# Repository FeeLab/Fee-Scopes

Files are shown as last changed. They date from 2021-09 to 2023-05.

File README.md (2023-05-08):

# Getting Started

animation of neural activity recorded in a mouse using the Kiloscope

Welcome to the repository on all things related to the Featherscope and Kiloscope, two light-weight head-mounted microscopes developed in the Fee lab at MIT. Our intent with this repository is to give you all the information you need to build your own scopes to use in your lab. We are also excited about people developing their own upgrades or even using elements of this project for their own microscope designs. Please let us know if you have any feedback or suggestions for improving these resources--we are always looking for ways to make this project more useful to the community!

The microscopes described in this repository are featured in [this bioRxiv paper](https://www.biorxiv.org/content/10.1101/2021.09.03.458947v2). All the analysis code in the paper can be found at [this repository](https://github.com/FeeLab/Microscope-Paper-Code), and the raw data from the paper is posted [here](https://academictorrents.com/details/aa2a3d2f5ff0b3974871db47db57bc3dabf3c192).

A fully functional system is comprised of the microscope itself, a DAQ and acquisition computer, a laser and associated illumination optics, and (optionally) a commutator for long-term recording. The components necessary for each of these subsystems are listed in `main_bom.ods` along with a cost breakdown.



# Microscope

Each microscope is built from small optical components mounted inside 3D printed parts. The optics needed for each microscope can be found under the Kiloscope and Featherscope tabs of `main_bom.ods`. The STEP files for the printed parts are located in the `body_components` folder. Technical details about the construction process can be found in the Methods section of the paper.

## Aspheric Lenses

lens assembly

The aspheric lens assemblies used in the Kiloscope are taken from replacement rear camera modules for the Samsung Galaxy S9 phone. These modules can be purchased online from 3rd party vendors, however the lenses then need to be carefully removed from the assembled housing. Instructions for removing the lenses from the modules can be found in `assembly_instructions`. The process should take about 20 minutes for an experienced assembler. Note that the lens material is very easy to scratch and difficult to clean, so be careful not to touch the lens faces during this process! When you have extracted the lens, you can store it safely in a PDMS device carrier (we reuse the containers that Edmund Optics ships their prisms in).

## Ground GRIN Lenses

GRIN lens

The tube lens used in the Featherscope is a GRIN lens purchased from Edmund Optics that has been ground down to a total length of 1 mm. Ideally we would have GRINTech, the manufacturer of the original lenses, make us custom lenses with the correct length to begin with. However, GRINTech and Inscopix have signed an anticompetitive exclusive distribution agreement for one-photon calcium imaging, so we have to be a little more creative about how we get these components. We purchase lenses from Edmund Optics (part number in BOM) and have them ground down to 1.00 mm by Pioneer Precision Optics, a custom optics company based in Massachusetts.

## Fiber Bundles

The fiber bundle used in the Featherscope is made by [Acrolite](https://www.acrolite.net/products/micro-fiber-optics), a company based in New York that specializes in making impressively tiny and intricate optical fiber bundles with custom potted termination geometries. They have a great engineering department and will work with you on custom solutions if you want to design a different illumination path.



## 3D Prints

We have had success ordering prints from [Rosenberg Industries](https://www.rosenbergindustries.com), a company based in Minnesota that specializes in prints for neuroscience implant devices. Parts are printed in Formlabs Grey resin at 25 micron resolution.



## Printed Circuit Boards

We order our image sensor boards from [Speedy Circuits](http://www.speedy-circuits.com.tw/), a board house in Taiwan that specializes in small run fabrication and assembly. We highly recommend the additional cost of board assembly unless you really want to practice your BGA soldering skills! Boards can be ordered using the gerber files found in the `python_pcb` folder.

Here are the specifications for the boards if you want to order them from another board house.

| Parameter       | Value       |
| -----------     | ----------- |
| Layer Count     | 6           |
| Copper Weight   | 1.1 mil external, 0.7 mil internal |
| Board Thickness | 500 micron |
| Dimensions | 8.2 x 14.0 mm |
| Number of Holes | 146 |
| Min Hole Size | 3 mil |
| Blind Vias | L1-L4 |
| Min Trace/Space | 3 mil |
| Vias in Pad | Epoxy Filled and Plated |
| Surface Finish | Immersion gold, 2 micron |

The board design files are free to view with Altium but require an Altium license to edit. If you are a student, you can obtain an [educational license](https://www.altium.com/education/student-licenses) for free. Let us know if you would like to convert the design files to an open-source format like KiCad and we would be happy to assist.

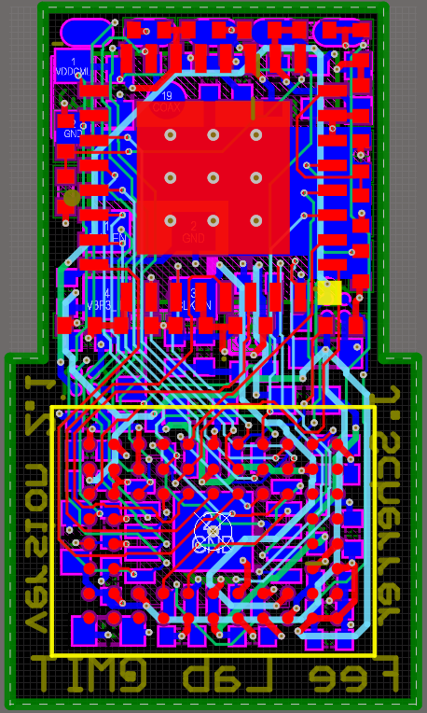
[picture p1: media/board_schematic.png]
Altium screenshot of schematic


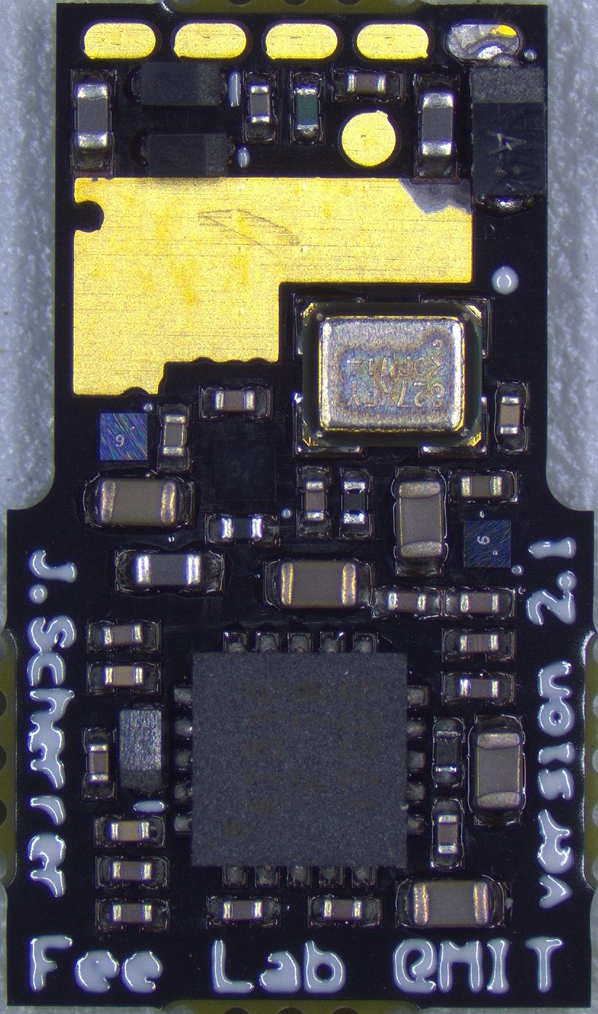
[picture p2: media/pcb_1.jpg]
top side of assembled pcb
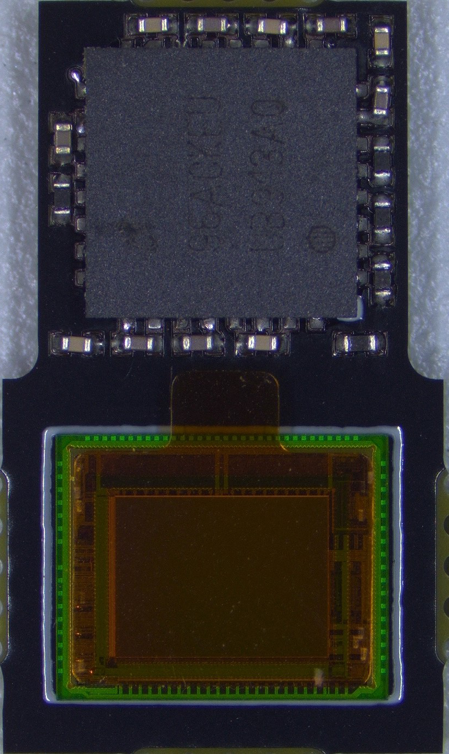
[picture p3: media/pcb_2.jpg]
bottom side of assembled pcb
 

## Assembly

Step-by-step instructions for assembling the microscopes are provided in `assembly_instructions`. Most components are secured using UV cure optical cement that can be purchased from [Edmund Optics](https://www.edmundoptics.com/f/norland-optical-adhesives/11818/) or a similar supplier. These instructions are a work in progress, so please don't hesistate to contact us if any of the steps are unclear!

## Programming

Firmware for the Attiny on the PCB can be found in `attiny_firmware`. Source code is included, with the exception of a section of `sensor_power_sequencing.c` that is restricted under NDA with Arrow, a distributor of ONSemi components. If you want access to the register settings contained in this section of the source code, contact an ONSemi distributor and request an NDA for the Python 480 programming notes.

The compiled code is contained in `Mscp_code/Release/Mscp_code.elf` and can be uploaded to the microcontroller using [Atmel Studio](https://microchipdeveloper.com/install:atstudio). We use [this programmer](https://www.microchip.com/en-us/development-tool/ATATMEL-ICE) but anything compatible with UPDI should work.

# DAQ System

## Hardware
The DAQ hardware is based on that of the [UCLA Miniscope](https://github.com/Aharoni-Lab/Miniscope-v4/wiki/DAQ-Hardware) and uses similar fabrication parameters. We had ours fabricated and assembled by [Seeed Studio](https://www.seeedstudio.com/) since these boards don't have as demanding specifications as the image sensor boards. Fabrication files can be found in the `DAQ` folder.

You will need to flash the firmware onto EEPROM before using the boards. Compile the DAQ firmware code in `cypress_firmware` using the [Cypress USB Suite](https://www.infineon.com/cms/en/design-support/tools/sdk/usb-controllers-sdk/ez-usb-fx3-software-development-kit/?utm_source=cypress&utm_medium=referral&utm_campaign=202110_globe_en_all_integration-software) and load it onto the board following the directions for the [UCLA Miniscope](https://github.com/Aharoni-Lab/Miniscope-DAQ-Cypress-firmware).

## Recording Software
The DAQ board presents itself to your computer as a webcam device, and for testing can be opened as a streaming device in [VLC](https://www.videolan.org/vlc/). For experiments, we acquire data from the microscope using [Bonsai](https://bonsai-rx.org/), a reactive programming languange designed for the multiple asynchronous data streams typical of behavioral neuroscience experiments. Bonsai has modules for recording from the UCLA Miniscope, Neuropixels, National Instruments devices, Arduinos, and various other data streams. We have written a module for our microscopes that can be downloaded from the Bonsai package manager. The module outputs video data in RGB565 format and allows for control of the image sensor gain. The source code can be found in `bonsai_module`.

An example Bonsai script for recording can also be found in `bonsai_module`. This script saves video from both the microscope and from an animal tracking camera simultaneously, while recording timestamps for each frame of both streams. Video is saved in the raw RGB565 format, but the script also performs realtime conversion to a human-interpretable grayscale image for online monitoring of the fluorescence signal.

Capture

# Illumination Optics

## Laser
Illumination light is provided by a multimode 473 nm laser similar to those used in optogenetics experiments. We use the MBL-473-50mW laser from [CNI Laser](http://www.cnilaser.com/), an optics company based in China with a wide range of turnkey optical systems for neuroscience applications. If you are planning on imaging at a different wavelength or have other specific requirements, they will probably be able to match your requirements.

## Coupling Optics
Light from the laser is coupled into the fiber using a system of optics detailed in the methods section of the paper and in `main_bom.ods`. Optics are assembled in a Thorlabs cage plate system for ease of alignment.

In the paper, we include a shutter so that illumination can be turned off when not recording to avoid photobleaching. However, the MBL-473-50mW laser from CNI has a TTL modulation input that can also be used to turn the laser on and off. The shutter is only needed in settings where the illumination power needs to be very stable over the course of the recording, as modulating the laser current results in temporary thermal instability in the laser cavity and a period of minor intensity variability.

The despeckler used in the paper has been discontinued since publication. Luckily, we have since developed a homemade despeckler that is both cheaper and more efficient than the previous despeckler, and can be built by hand in a few hours. We will post construction details as soon as we have the release version finalized, so follow this space for more details.

# Commutator
For recording sessions that last 30 minutes or less, you may be able to use a static recording setup without the animal twisting the tether excessively. However, for longer-term recordings or with very active or sensitive animals (e.g. birds), a commutator will be necessary to avoid tether wrapping issues. 

We have designed an actively driven commutator for the microscopes that simultaneously transmits power, data, and illumination light. Design files, along with notes on assembly, can be found in the `commutator` directory as well as in `main_bom.ods`.

## Machined components
The commutator base consists of two custom machined aluminum plates. Drawings for these plates can be found in the `commutator` folder. They can be fabricated by your favorite machine shop or online machining service (we use [Protolabs](https://www.protolabs.com/services/cnc-machining/)).

## PCB
The commutator PCB provides regulated power to the microscope and sends a torque signal to the motor controller. It is a simple two-layer board and can be fabricated by [OSHPark](https://oshpark.com/). Design files can be found in `commutator/sensor_board` in EAGLE format. Autodesk offers free educational licenses for EAGLE.

## Motor Controller Box
The commutator is driven by a Faulhaber DC motor controlled by a custom motor driver. The PCB for the driver can be found in `commutator/motor_controller` and can be fabricated by OSHPark. Components and assembly notes for the driver box can also be found in `commutator/motor_controller`.

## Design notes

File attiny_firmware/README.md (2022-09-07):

# THIS CODE CONTAINS MATERIAL PROTECTED UNDER NDA WITH ARROW, DO NOT RELEASE THIS TO THE PUBLIC!!!!

# Firmware for the ATtiny 816 MCU onboard the 'feather-scope' fee-scope, Revision 2.0

This firmware programs the onboard attiny 816 to act as a I2C to SPI bridge,
sample analog inputs, and finally transmit analog samples along with sync
information to the SERDES. This version of the firmware is intended to control
the ON-semi Python 480 image sensor, featherscope revison 2.0.

## Microcontroller's Behavior and Responsibilities

The ATTiny 816 microcontroller on the pico-scope is responsible for three things:

1. Initial configuration of the E2V image sensor
2. Conversion of I2C messages from the serializer to SPI messages to the E2V imaging sensor
3. Sampling its analog inputs and transmitting ADC reads to the serializer

Each of these functions are controlled through the MCU's I2C interface. The code
controlling the I2C interace is in `twi_slave.c`. In brief, the ATTiny 186
responds to two I2C addresses.

| Sub Device         | Description                                                          | I2C (write) address |
|--------------------|----------------------------------------------------------------------|---------------------|
| I2C -> SPI Bridge  | Convert I2C commands from serializer to SPI commands to image sensor | `B8h`               |
| ADC (self)         | Control ADC subsystem                                                | `98h`               |

### I2C -> SPI Bridge

The E2V image sensor can be accessed via the ATTiny's I2C interface. Reads and
writes to registers on the E2V are accomplished by addressing the same
'register' on the I2C bridge device. This is true for all registers except the
reserved register, `FFh`, which triggers the reset and initial configuration of
the E2V sensor.

| Register    | Description    | Effect                                                               |
|-------------|----------------|----------------------------------------------------------------------|
| `00h`-`FEh` | Pass through   | Reads and writes to the I2C device are repeated on the SPI interface |
| `FFh`       | Initialization | E2V image sensor is reset and configured according to EEPROM values  |

### ADC Subdevice

The ADC can be controlled via the 'self' device by writing to the following registers:

| Register Name     | Address | bit fields            | description                                                                 |
|-------------------|---------|-----------------------|-----------------------------------------------------------------------------|
| ADC control       | `01h`   | [0000-00me]           | e bit is enable (1 is on), m bit requests multiplexing (sample both inputs) |
| ADC sample period | `02h`   | [bbbb-bbbb-bbbb-bbbb] | Number of CPU clock cycles between ADC samples, two bytes                   |

#### ADC Behavior

The ADC is read after `N` CPU clock cycles, where `N` is set by the ADC sample
period register. It must be at least `0034h`.

The USART does not use inverted output (e.g. low is 0), and transmits the least
significant bit first.

If multiplexing is requested, the ADC will sample AIN8 and AIN9 in round robin.
Otherwise AIN8 alone is sampled.

### USART output of ADC reads

ADC reads will be transmitted over the USART interface with synchronous serial
output. ADC reads are transmitted in two bytes. The LSB of the ADC read is
transmitted in the first byte. The second byte is [ffprssaa], most significant
bit on the left, where ff is the frame indicator (`01b`), p is the adc input bit
(0 for AIN8, 1, for AIN9), r is reserved (intended for overflow), ss are the
sync variables (LV - msb, FV -lsb) from frame enable and line enable, and aa are
the two most significant bits from the ADC read, least significant bit in the
least significant position.

Each byte is transmitted in a 10 bit frame, with the first bit being the frame
start indicator (always low), and the last bit being the frame start indicator
(always high), and the eight data bits will be in between. The TXD
(transmission) and XCK (transmission clock) lines of the USART peripheral will
be used to transmit the data. The transmission clock will idle low, and the
on the TXD line will be valid on the rising edge of the clock signal. The data
will change on the falling edge of the clock signal. The TXD line idles high.The
8 data bits will be transmitted most significant bit first.

## Building
Compile the code with `release` configuration prior to programming the
microcontroller, unless you're debugging with the UPDI interface.

ADC timings are only tested with `release` code, so use `debug` at your own risk.

## Programming
Some of the startup register settings for the Python 480 image sensor are
proprietary and can only be accessed by signing a non-disclosure agreement with
an ONSemi distributor. We are legally obligated to redact portions of the source
code containing this information. The compiled code is contained in the Release
folder and can be uploaded directly to the microcontroller using Atmel Studio.

## High level overview of the code

Functionality is mostly implemented through interrupts. The I2C (called TWI by
Atmel) subsystem is exclusively driven by interrupts. ADC sampling is not done
with interrupts, but instead polls the ADC conversion register for results.
However, the ADC programming is controlled by global variables that are set by
I2C interrupts. E2V intialization makes heavy use of data EEPROM. See programming
notes for caveats about writing these EEPROM values. Many functions are
'inlined', and therefore appear in header files.

| functionality      | files                                     |
|--------------------|-------------------------------------------|
| I2C -> SPI bridge  | `twi_slave`, `spi_master`                 |
| E2V initialization | `spi_master`, `twi_slave`                 |
| ADC control        | `adc`, `usart_out`, `twi_slave`, `main`   |

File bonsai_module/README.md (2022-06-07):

# Bonsai.FeatherScope
[Bonsai](http://bonsai-rx.org/) package for controlling and acquiring data from the FeatherScope.

## Upstream
This project is a fork of [Bonsai.Vision.CameraCapture](https://bitbucket.org/horizongir/bonsai/src/43c4072273efcaff77e429296c2d6d8756ec07c7/Bonsai.Vision/CameraCapture.cs?at=default&fileviewer=file-view-default)
and [Bonsai.Miniscope](https://github.com/jonnew/Bonsai.Miniscope)

## License
[MIT](https://opensource.org/licenses/MIT)

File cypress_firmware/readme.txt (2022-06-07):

Feescope firmware for EZ-USB FX3 HD 720P DAQ board. Only for use with the
kiloscope and featherscope.

Modifications to stock firmware made by Galen Lynch.

Follow instructions in cypress EZ_USB FX3 SDK
(https://www.cypress.com/documentation/software-and-drivers/ez-usb-fx3-software-development-kit)
for installing the software environment needed to build the firmware and program
the DAQ board.

Details on programming the DAQ board, which is a slightly modified UCLA
miniscope v3 DAQ board, can be found on the UCLA miniscope wiki for miniscope v3
(http://miniscope.org/index.php/Software_and_Firmware_Setup).

Cypress README below:

                        CYPRESS SEMICONDUCTOR CORPORATION

                            EZ-USB FX3 UVC CAMERA KIT

FX3 UVC KIT FIRMWARE
--------------------

    1. Introduction:
    ----------------

    This project facilitates implementing a complete 720p Video solution using
    the EZ-USB FX3 device and an Image Sensor that supports YUY2 image streaming
    over a parallel synchronous interface.

    This Eclipse project contains the firmware application code that implements
    the Image Sensor interface and the USB Video Class (UVC) control and streaming
    logic. This firmware application supports streaming video in the following
    formats:

        1. Uncompressed HD 720p (1280 * 720) resolution video at 30 frames per
           second (fps) over a USB 3.0 link.
        2. Uncompressed VGA (640 * 480) resolution video at 15 frames per second
           (fps) over a USB 2.0 link.

    Please refer to the "AN75779: Interfacing an Image Sensor to EZ-USB FX3 in a USB
    video class (UVC) Framework" application note (http://www.cypress.com/?rID=62824)
    for a detailed design description of this application.

    2. Files:
    ---------

        1. uvc.c                : Main source file implementing the UVC control and
                                  streaming logic.

        2. uvc.h                : Configuration parameters and constant definitions
                                  for the UVC application firmware.

        3. cyfxuvcdscr.c        : USB descriptors used by the UVC firmware.

        4. camera_ptzcontrol.c  : Extension stubs for implementation of camera controls
                                  like Pan, Tilt and Zoom.

        5. camera_ptzcontrol.h  : Variable and function declarations for the Pan, Tilt
				  and Zoom control stubs.

        6. sensor.c             : Function placeholders and I2C driver functions to configure/control
                                  the image sensor through the I2C interface on FX3.

        7. sensor.h             : Interface declarations for the image sensor driver.

        8. cyfxgpif2config.h    : Configuration data generated by GPIF II Designer.

        9. cyfxtx.c             : RTOS porting layer for the EZ-USB FX3 SDK.

        10. cyfx_gcc_startup.S  : Startup file for the GNU ARM tool-chain. This only
                                  clears the BSS segment and then jumps to the main
                                  function.

    3. Notes on Application Porting:
    --------------------------------

    This UVC video streaming application can be ported to work with virtually
    any image sensor with parallel interface.

    The general procedure for porting the application to a particular sensor is:

    1. Identify the sensor control mechanism (I2C, SPI etc.) and make appropriate
       changes to the sensor.c file. Code can be added to the SensorI2cBusTest()
       function to verify whether the sensor is accessible through the firmware.
       Once functionality is verified, implement the sensor initialization function
       SensorInit () and the resolution settings functions: SensorScaling_HD720p_30fps ()
       and SensorScaling_VGA () or whichever resolution is required.
    2. Identify the signal interface between the sensor and FX3, and update the
       GPIF-II state machine accordingly. You may require to update the GPIF-II
       initialization code in uvc.c (CyFxUvcAppGpifInit and CyFxGpifCB functions)
       as well.
    3. Update the code for handling UVC controls like brightness, pan, tilt and
       zoom (uvc.c and camera_ptzcontrol.c).

    Please refer to the AN75779 for a detailed description on the design process.

    4. Updating to a new FX3 SDK version:
    -------------------------------------

    The cyfxtx.c and cyfx_gcc_startup.S files used here are taken from the FX3 SDK
    release. This version of the application makes use of FX3 SDK release version
    1.3.3.

    When updating the application to work with a new SDK version, you need to copy
    the latest cyfxtx.c and cyfx_gcc_startup.S files from the new SDK into this
    project. You will also need to follow the instructions for porting to the new
    SDK that are included in the "Getting started with the FX3 SDK" document.

    5. Guidelines to run UVC extension unit host application:
    ---------------------------------------------------------

    The extension unit supports Firmware version control. User can set or get firmware 
    version. Run the uvc_extension_app_x64/x86 application. The firmware enumerates as
    a "FX3" device. If the FX3 device is detected, user can select 1/2 to set/get 
    firmware version. 
    
    1. Set firmware version: By default, application sets the firmware version to 
       2.2 and build date to 12/20/18. Host application needs to be modified to set 
       any other firmware version.
    2. Get firmware version: Gives the current firmware version

    Host application is uploaded on the Cypress Community forum (Refer App note). 
    Based on the requirements, users can update the UVC host application. If the default 
    app note firmware is loaded, the host application fails with the following print:
    Function: SetGetExtensionUnit, ks_control->KsProperty(...) failed, Error code: 0x80070492

    6. Tests done to check video stability:
    ---------------------------------------

    Video stability is important and a video freezing in a UVC host application is 
    not a good sign. One might have to disconnect and re-connect the device to 
    recover from such failures. Video may freeze when USB host is slower or 
    Sensor/Image signal processor goes into a bad shape. The firmware has a commit buffer 
    failure event and video timer to handle this. There will be a drop in few frames and 
    the video re-starts. Tests done to recover from such failures:
    
    1. Stream video for 5 hours on a Windows PC in USB2 and USB3 mode. 
          a. PC: Lenovo modelT530
          b. OS: Win 10 Version 1607 (OS Build 14393.1480)
          c. Application: eCAMView version 1.0.63.349
          d. Hardware: CYUSB3KIT-003, CYUSB3ACC-004 and MT9M114 
    2. Stream video for 5 hours on a MAC PC in USB2 and USB3 mode. 
          a. PC: Mac book
          b. OS: Mac OS Sierra 10.12
          c. Application: Wirecast version 6.0.5
          d. Hardware: CYUSB3KIT-003, CYUSB3ACC-004 and MT9M114

    7. USB CV test on a Windows PC:
    -------------------------------

    USB CV test is standard command verifier test from usb.org. This test validates the 
    descriptor and UVC functionality. Following test were carried out and all the tests
    passed successfully.
    
    1. USB 2 CV test. Application: USB2 CV version 1.5.2.3. Tests done:
          a. Chapter 9
          b. Current Measurement
          c. Device summary
          d. UVC Descriptor
          e. UVC functionality
          f. UVC encoding unit test
          g. UVC H.264 test
    2. USB 3 CV test. Application: USB 3 GenX CV v2.1.5.0. Tests done:
          a. Chapter 9
          b. Current Measurement
          c. Device summary
          d. UVC Descriptor
          e. UVC functionality
[]

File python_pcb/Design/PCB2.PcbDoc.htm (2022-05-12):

Reporting Options

# File in Previous Format

Date | : | 5/11/2022
Time | : | 9:59:11 AM
Filename | : | C:\Users\Joe\Documents\Fee-Scopes\python_pcb\Design\PCB2.PcbDoc

Version | Warning

This file was generated by an earlier version of the software

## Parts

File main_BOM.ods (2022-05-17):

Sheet: Summary
sub-assembly | featherscope | kiloscope
microscope | $896.59 | $807.03
commutator | $1,651.03 | $1,651.03
coupling optics | $1,792.81 | $1,792.81
laser | $995.00 | $995.00
TOTAL | $5,335.43 | $5,245.87

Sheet: featherscope
microscope | Total cost: | $896.59
description | supplier | part number | cost (per) | quantity | line cost
3D printed bodies | Rosenberger Industries | N/A | $10.00 | 1 | $10.00
tube lens (1.0mm length) | Pioneer Precision Optics | N/A | $120.00 | 1 | $120.00 | Edmund Optics #64-538, ground down to 1.00 mm length
objective lens | Edmund Optics | 64-538 | $62.50 | 1 | $62.50
prism, 300 um width | Edmund Optics | 66-770 | $97.00 | 1 | $97.00
custom fiber bundle, 38 cm length, 300 micron diameter | Acrolite | N/A | $115.00 | 1 | $115.00
dielectric filter, 3x3x0.5 mm | Chroma | ET525/50m |  | 1
Wratten filter | Knight Optical | 494FWP7575 | $62.55 | 1
000-120 screw, 1/4" | McMaster | 91794A755 | $2.50 | 1 | $2.50
000-120 nut | McMaster | 90001A302 | $2.76 | 1 | $2.76
polyurethane foam, 1/16" thick | Mcmaster | 86375K132 | $7.54 | 1 | $7.54
polyurethane foam, 1/8" thick | McMaster | 86375K133 | $9.36 | 1 | $9.36
0.004" stainless shim stock, 18-8 hardened | McMaster | 9011K815 | $7.59 | 1 | $7.59
assembled circuit board | Speedy Circuits and others | N/A | $417.00 | 1 | $417.00
coax | Cooner Wire | CW6563 | $16.00 | 1 | $16.00
DC wire | Cooner Wire | CZ1174 |  | 1 | $0.00
SMC plug | Digikey | J10183-ND | $9.34 | 1 | $9.34
DC connector | Omnetics | Nano Strip | $20.00 | 1 | $20.00

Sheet: kiloscope
kiloscope | Total cost: | $807.03
description | supplier | part number | cost (per) | quantity | line cost
3D printed bodies | Rosenberger Industries | N/A | $10.00 | 1 | $10.00
3D printed baseplate | Rosenberger Industries | N/A | $5.00 | 1 | $5.00
aspheric lens assemblies | MMOBIEL | https://www.amazon.com/MMOBIEL-G960-Replacement-Screwdriver-Installation/dp/B07DTH724D | $15.00 | 2 | $30.00
prism, 300 um width | Edmund Optics | 66-770 | $97.00 | 1 | $97.00
200 micron multimode fiber, 2 meters | Thorlabs | FP200URT | $3.58 | 1 | $3.58
dielectric filter, 4x4x0.5 mm | Chroma | ET525/50m | $200.00 | 1 | $200.00
Wratten filter | Knight Optical | 494FWP7575 | $62.55 | 0.1 | $6.26
000-120 screw, 1/4" | McMaster | 91794A755 | $2.50 | 1 | $2.50
000-120 nut | McMaster | 90001A302 | $2.76 | 1 | $2.76
0.004" stainless shim stock, 18-8 hardened | McMaster | 9011K815 | $7.59 | 1 | $7.59
assembled circuit board | Speedy Circuits and others | N/A | $417.00 | 1 | $417.00
coax | Cooner Wire | CW6563 | $16.00 | 1 | $16.00
DC wire | Cooner Wire | CZ1174 |  | 1 | $0.00
SMC plug | Digikey | J10183-ND | $9.34 | 1 | $9.34
DC connector | Omnetics | Nano Strip |  | 1 | $0.00

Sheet: tools
tools/supplies | Total cost: | $117.86
description | supplier | part number | cost (per) | quantity | line cost
reamer for kiloscope | mcmaster | 8803A576 | $28.44 | 1 | $28.44
reamer for featherscope | mcmaster | 8803A156 | $18.42 | 1 | $18.42
Norland 61 cement | edmund | 37-322 | $35.50 | 1 | $35.50
Norland 61 cement | edmund | 36-425 | $35.50 | 1 | $35.50

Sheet: commutator
commutator | Total cost: | $1,651.03
description | supplier | part number | quantity | cost per piece | line cost
optical rotary joint | Thorlabs | RJ1 | 1 | $512.43 | $512.43
cage rods | Thorlabs | ER6-P4 | 1 | 33.86 | 33.86
cage plate | Thorlabs | CP33 | 1 | 16.89 | 16.89
0.50 NA FC/PC patch cable | Thorlabs | M123L01 | 2 | 87.21 | 174.42
fiber mating sleeve | Thorlabs | ADAL1 | 2 | 4.96 | 9.92
ceramic fiber ferrule | Thorlabs | CFX270-10 | 3 | 6.56 | 19.68
pulley | McMaster | 6284K11 | 1 | 16.67 | 16.67
1/4"-20 standoff | McMaster | 91125A652 | 4 | 3.85 | 15.40
2-56 standoff | McMaster | 91115A115 | 2 | 2.34 | 4.68
pipe clamp | McMaster | 11355T62 | 1 | 3.22 | 3.22
drive belt | McMaster | 8060K16 | 1 | 4.90 | 4.90
bearing | McMaster | 57155K329 | 1 | 9.40 | 9.40
tubing | McMaster | 6100K471 | 1 ft | 8.32 | 8.32
magnet | McMaster | 5862K105 | 1 | 1.65 | 1.65
3/8" tube | McMaster | 3044K603 | 1 ft | 15.17 | 15.17
shielded twisted pair | Digikey | 55A1121-26-6/9-9-DS-ND | 4 ft | 5.37 | 21.48
SMC connector | Digikey | ACX1507-ND | 1 | 5.02 | 5.02
DC connector | Omnetics | Nano Strip | 1 | 20.00 | 20.00
slip ring | Moflon | MSP1069 | 1 | 185.00 | 185.00
machined plate | protolabs | N/A | 2 | 250.00 | 500.00
bearing column | ??? |  |  |  | 0.00
commutator motor driver | digikey | see BOM | 1 | $38.98 | 38.98
hall sensor board components | digikey | see BOM | 1 | $33.94 | 33.94
shaft bearings | McMaster | 60355K504 | 2 | $5.78 | 11.56

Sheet: coupling optics
coupling optics | Total price: | $1,792.81
description | supplier | part number | quantity | cost per piece | line cost | comment
rods (pack of four) | Thorlabs | ER4-P4 | 1 | $27.79 | $27.79
shutter mount | Thorlabs | SHCP025 | 1 | 42.20 | 42.20 | OPTIONAL
shutter | Thorlabs | SHB025 | 1 | 938.20 | 938.20 | OPTIONAL
lens mounts | Thorlabs | CP1M09 | 4 | 40.04 | 160.16
1:1 relay | Thorlabs | C280TMD-A | 2 | 85.49 | 170.98
despeckler output collimator | Thorlabs | A397TM-A | 1 | 98.47 | 98.47
output fiber coupling | Thorlabs | C230TMD-A | 1 | 73.05 | 73.05
4 mm cage plates | Thorlabs | CP4S | 2 | 19.78 | 39.56
1" cage plate | Thorlabs | CP33 | 2 | 16.89 | 33.78
FC/PC fiber adaptor | Thorlabs | SM1FC | 2 | 31.38 | 62.76
speckle reducer | Edmund Optics | 88-392 | 1 | 635.00 | 635.00 | DISCONTINUED--CNI replacement
axicon | Thorlabs | AX1220-A | 2 | 221.71 | 443.42
axicon cage plate | Thorlabs | CP14 | 2 | 23.92 | 47.84

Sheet: laser
laser | Total price: | $995.00
description | supplier | part number | quantity | cost per piece | line cost | comment | in stock?
473 nm laser | CNI Laser, inc. | MBL-III-473 | 1 | $995 | $995

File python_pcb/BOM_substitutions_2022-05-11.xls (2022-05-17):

Comment | Description | Designator | Footprint | LibRef | Quantity
Murata GRM033C71C104KE14D | CAP 0.1uF 16VDC X7S 10% SMD 0201 | C1, C2, C3, C4, C5, C6, C9, C10, C12, C13, C16, C18, C24, C28, C30, C32, C36, C37, C40 | PCB-v6eq6etc9p7u7qdkgnno-1 | CMP-cc290632c88a13ee-3 | 19
Murata ZRB15XR61A106ME01D | Cap Ceramic 10uF 10V X5R 20% SMD 0402 85°C Paper T/R | C7, C11, C14, C20, C21 | PCB-uspfzztrpe7hn2xlyjz9-1 | CMP-eacb22ede71a350c-8 | 5
Murata GRM033R71A103KA01D | CAP CER 10000PF 10V 10% X7R 0201 | C8, C15, C19, C25, C27, C29, C33, C34 | PCB-v6eq6etc9p7u7qdkgnno-1 | CMP-19299660-4 | 8
AVX F981A475MUALZT | Cap Tant Solid 4.7uF 10V U CASE 20% (1.1 x 0.6 x 0.55mm) SMD 1106-06 25Ohm 125°C T/R | C17, C26, C31 | PCB-t0dwbiosd2m6unyihqym-1 | CMP-b7737c8c1b6d68b4-6 | 3
Murata GRM033R60J105MEA2D | Multilayer Ceramic Capacitor, GRM Series, 1 uF, 20%, X5R, 6.3 V, 0201 [0603 Metric] | C22, C23, C39 | PCB-v6eq6etc9p7u7qdkgnno-1 | CMP-7dcab586fd61a20d-5 | 3
AVX F981A226MMALZT | Capacitor, SMD, Resin Molded, High CV Undertab, F98 Series, 10Vdc, 22uF, ±20%, Case M (EIA0603), 1.6x0.85x0.8mm, 60ºC... | C35 | PCB-yxd74t6run51sg1ha7ug-1 | CMP-ed552659f9643292-2 | 1
Murata GRM033R60J473KE19D | Multilayer Ceramic Capacitors MLCC - SMD/SMT 0201 0.047uF 6.3volts X5R 10% | C38 | PCB-v6eq6etc9p7u7qdkgnno-1 | CMP-131779-4 | 1
BLM15AX601SN1D | FERRITE BEAD 600 OHM 0402 1LN | FB1 | MURA-BLM15-CHIP-2_V | CMP-886590-4 | 1
BLM15AX102SN1D | Chip Ferrite Bead for General Use, 1000 Ohm, 350 mA, -55 to 125 degC, 1 x 0.5 x 0.55 mm SMD, Tape and Reel | FB2, FB3 | MURA-BLM15-CHIP-2_V | CMP-886590-4 | 2
ERJ-1GNF4702C | RES SMD 47K OHM 1% 1/20W 0201 | R1 | PCB-7g93mzch2qc2q3jid3ok-1 | CMP-1848656-4 | 1
ERA-1AEB152C | Thin Film Resistors - SMD 0201 1.5Kohm 0.1% 25ppm | R2 | PCB-7g93mzch2qc2q3jid3ok-1 | CMP-1848326-4 | 1
CRCW02011K80JNED | Thick Film Resistors - SMD 1/20watt 1.8Kohms 1% 200ppm | R3 | PCB-7g93mzch2qc2q3jid3ok-1 | CMP-1848326-4 | 1
ERJ-U01F49R9C | Thick Film Resistors - SMD 0201 1% 49.9ohm Anti-Sulfur AEC-Q200 | R4 | PCB-7g93mzch2qc2q3jid3ok-1 | CMP-1848375-4 | 1
ERJ-1GNF1002C | Res Thick Film 0201 10K Ohm 1% 0.05W(1/20W) ±200ppm/C Molded SMD Paper T/R | R5, R6 | PCB-7g93mzch2qc2q3jid3ok-1 | CMP-1848298-4 | 2
ERJ-1GNF1003C | Res Thick Film 0201 100K Ohm 5% 1/20W ±200ppm/C Molded SMD Pressed Carrier T/R | R7 | PCB-7g93mzch2qc2q3jid3ok-1 | CMP-1848300-4 | 1
Panasonic ERJ-1GEJ332C | Res Thick Film 0201 3.3K Ohm 5% 1/20W ±200ppm/C Molded SMD Paper T/R | R8, R9 | PCB-7g93mzch2qc2q3jid3ok-1 | CMP-1848326-4 | 4
Microchip ATTINY816-MFR | 8-bit Microcontroller, 20MHz, 8KB, QFN20, Ind 125C, Green, in a 20 pin VQFN pkg | U1 | PCB-hv4cq49t2e9uf1npj5by-1 | CMP-1cb5d12d1e47c372-8 | 1
Python 480 | image sensor from ONSemi | U2 | Python 480 | CMP-zuljd18wlr9in3443qu3-3 | 1
KC2520Z66.6667C1KX00 | Standard Clock Oscillators MEMS Oscillator Low PWR LVCMOS -40C-105C | U3 | ASD | ASD oscillator | 1
ON Semiconductor NCP163AFCT330T2G | LDO Regulator, 250 mA, Ultra-High PSRR, Ultra-Low Noise 3.3 V, Active Discharge | U4, U5 | PCB-ng8273kv6qqz2xsov2q1-1 | CMP-c6890ab21004194e-8 | 2
DS90UB913ATRTVRQ1 | 25-100MHz 10/12-Bit FPD-Link III SERIALIZER 32-WQFN -40 to 105 | U6 | PCB-l2nnig1h4ckv44w98gav-1 | CMP-1f96d75fdae3c051-6 | 1
MAX44281OANS+T | Operational Amplifiers - Op Amps 4-bump Op Amp | U7 |  |  | 1

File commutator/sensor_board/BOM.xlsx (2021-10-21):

FB02 | MPZ1608S471ATA00 | Ferrite Beads Ferrite Beads 470ohms 1A 150mOhms 0603 Ferrite Chip
C16 | EEH-ZC1V221P | Aluminum Organic Polymer Capacitors Aluminum Organic Polymer Capacitors 35VDC 220uF 20% AEC-Q200
C1, C7, C12. C14 | F951A476KBAAQ2 | Tantalum Capacitors - Solid SMD Tantalum Capacitors - Solid SMD 47uF 10V 10% 1411 3.5x2.8x1.8mm
C6, C13 | CC0805KKX7R6BB106 | Multilayer Ceramic Capacitors MLCC - SMD/SMT Multilayer Ceramic Capacitors MLCC - SMD/SMT 10V 10uF X7R 0805 10%
C2, C8, C15 | CC0603KRX7R6BB105 | Multilayer Ceramic Capacitors MLCC - SMD/SMT Multilayer Ceramic Capacitors MLCC - SMD/SMT 10V 1uF X7R 0603 10%
U1, U5 | TPS7A4701RGWT | LDO Voltage Regulators LDO Voltage Regulators 36V 1A 4.17uVRMS RF LDO VTG Reg
U2 | ISL21090BFB825Z-TK | Voltage References Voltage References PBFREE PRECISION 2 5V LW V FGA"F 0 01%
C3, C10 | GRM155R71C104KA88J | Multilayer Ceramic Capacitors MLCC - SMD/SMT Multilayer Ceramic Capacitors MLCC - SMD/SMT 0.1uF 16 volts 10%
R1 | ERJ-2GEJ162X | Thick Film Resistors - SMD Thick Film Resistors - SMD 0402 1.6Kohms 5% AEC-Q200
U4 | ISL28634FVZ | Instrumentation Amplifiers Instrumentation Amplifiers 5V Instr., Op-Amp Zero-Drift
C9 | GRM155R71C103KA01D | Multilayer Ceramic Capacitors MLCC - SMD/SMT Multilayer Ceramic Capacitors MLCC - SMD/SMT SUGGESTD REPLACEMENT 81-GRM033R71C103KE4
R2, R3 | FC0402E50R0BST1 | High Frequency/RF Resistors High Frequency/RF Resistors 50ohms 0.1% 25ppm
S1, S2 | CJS-1201 | Slide Switches smd jumper switch, J hook, with detent,washable

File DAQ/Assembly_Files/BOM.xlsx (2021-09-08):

C6, C8, C11, C14, C16, C19, C25, C28, C29, C31, C38, C43, C44, C47, C49, C51, C60, C62, C64, C66, C82 | GRM188R71H103KA01D | 21 | www.digikey.com
C22, C27 | GRM155R71E473KA88D | 2 | www.digikey.com
C21, C26, C77 | GRM155R71C104KA88D | 3 | www.digikey.com
C1, C2, C3, C7, C9, C12, C15, C17, C20, C24, C32, C37, C40, C41, C42, C45, C46, C48, C50, C52, C54, C56, C58, C59, C61, C63, C65, C69, C78, C79, C84 | CL10B104KO8NNNC | 31 | www.digikey.com
C4, C5, C70 | GRM188R61A105KA61D | 3 | www.digikey.com
C53, C74 | GRM188R61C225KE15D | 2 | www.digikey.com
C10, C23, C67, C68, C75, C76 | GRM188R61C475KE11D | 6 | www.digikey.com
C83 | TACL106M010XTA | 1 | www.digikey.com
C30, C71, C72 | GRM188R61C106MA73D | 3 | www.digikey.com
C13, C18, C39, C55, C57 | GRM188R60J226MEA0D | 5 | www.digikey.com
C33, C34 | TCTAL0J107M8R | 2 | www.digikey.com
C35, C36 | T495D337K010ATE125 | 2 | www.digikey.com
R44, R45 | RC0603FR-070RL | 2 | www.digikey.com
R6, R7, R8, R9. R10. R11, R13, R15, R16, R17, R18, R19, R20, R21, R22, R23, R24, R25, R29, R62, R67 | RC0603FR-0722RL | 21 | www.digikey.com
R59 | RC0603FR-0733RL | 1 | www.digikey.com
R34, R35 | RC0402FR-0749R9L | 2 | www.digikey.com
R64, R65, R66 | RC0603FR-07100RL | 3 | www.digikey.com
R5 | RC0603FR-07200RL | 1 | www.digikey.com
R52 | RC0603FR-07430RL | 1 | www.digikey.com
R50, R60, R61, R63, R56, R57 | RC0603FR-071KL | 6 | www.digikey.com
R55 | RC0603FR-071K15L | 1 | www.digikey.com
R12, R14 | RC0603FR-072KL | 2 | www.digikey.com
R53 | RC0603FR-073K57L | 1 | www.digikey.com
R4 | RC0603FR-076K04L | 1 | www.digikey.com
R1, R2, R3, R26, R28, R31, R36, R37, R38, R39, R40, R41, R42, R43, R47, R48, R49, R51 | RC0603FR-0710KL | 18 | www.digikey.com
R46 | RC0603FR-073KL | 1 | www.digikey.com
R54 | RC0603FR-0730K1L | 1 | www.digikey.com
R58 | RC0603FR-07100KL | 1 | www.digikey.com
R33 | RC0603FR-071ML | 1 | www.digikey.com
L1, L2 | BLM21PG221SN1D | 2 | www.digikey.com
L3, L4, L11 | BLM18KG601SN1D | 3 | www.digikey.com
L5 | LQM21PN2R2MC0D | 1 | www.digikey.com
L6, L7, L8, L9, L10 | MPZ2012S601AT000 | 5 | www.digikey.com
L12 | ASMPH-0805-4R7M-T | 1 | www.digikey.com
L13 | CBC3225T101MR | 1 | www.digikey.com
*1 | XLH536026.000000I | 1 | www.digikey.com
u10 | SG-3040LC 32.7680KB3: PURE SN | 1 | www.digikey.com
U1 | SP3010-04UTG | 1 | www.digikey.com
U2 | CYUSB3014-BZXC | 1 | seeedstudio.com/opl.html
U3 | NCP361SNT1G | 1 | www.digikey.com
U4 | DS90UB914ATRHSTQ1 | 1 | www.digikey.com
U6 | TPS74801DRCR | 1 | www.digikey.com
U7 | TPS76801QDR | 1 | www.digikey.com
U8 | TPS62231DRYT | 1 | www.digikey.com
U13 | ADN4663BRZ | 1 | www.digikey.com
U15, U16, U18 | MMBT3904-TP | 3 | www.digikey.com
J1 | 897-10-010-40-300002 | 1 | www.digikey.com
J2 | PJ-036BH-SMT-TR | 1 | www.digikey.com
SW1, SW2, SW3 | 218-4LPST | 3 | www.digikey.com
SW4 | B3F-1002 | 1 | www.digikey.com
U11, U12, U14 | LTST-C190KGKT | 3 | www.digikey.com
J3, J4, J5 | CONSMA002 | 3 | www.digikey.com
U5 | DILB8P-223TLF | 1 | www.digikey.com
K1, K2, K3 | 67996-206HLF | 3 | www.digikey.com
J9 | 5-146280-3 | 1 | www.digikey.com
J6 | 10029449-111RLF | 1 | www.digikey.com

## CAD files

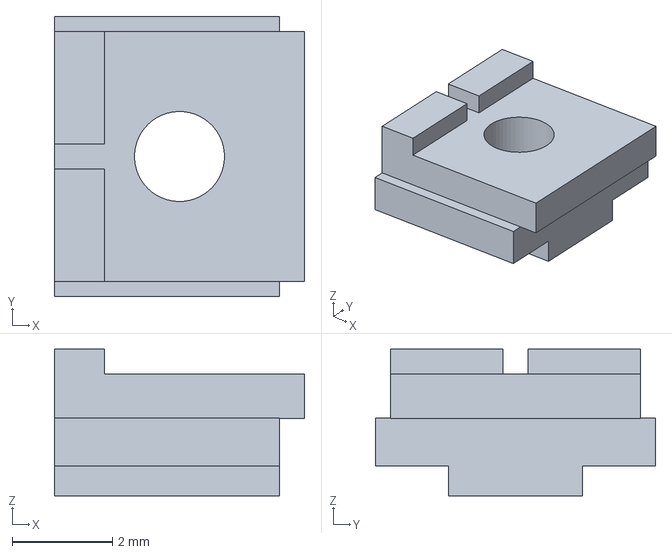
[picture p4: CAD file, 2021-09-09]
body_components/featherscope/lower_subassembly.step
5.00 x 5.60 x 2.93 mm

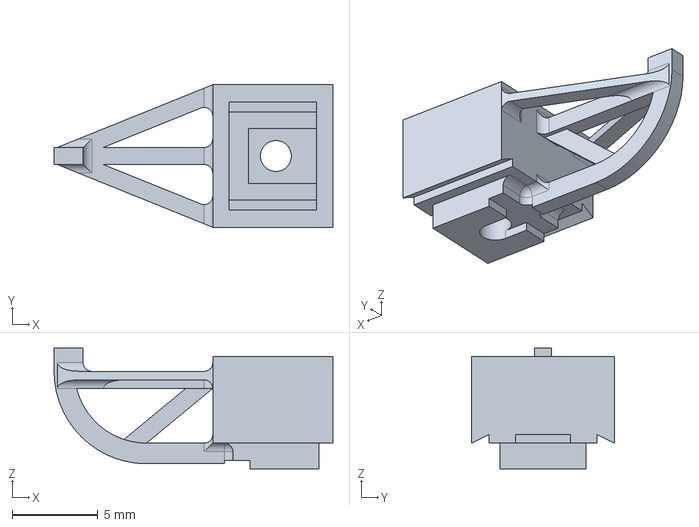
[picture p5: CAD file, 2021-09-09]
body_components/featherscope/upper_subassembly.step
16.2 x 8.30 x 7.03 mm

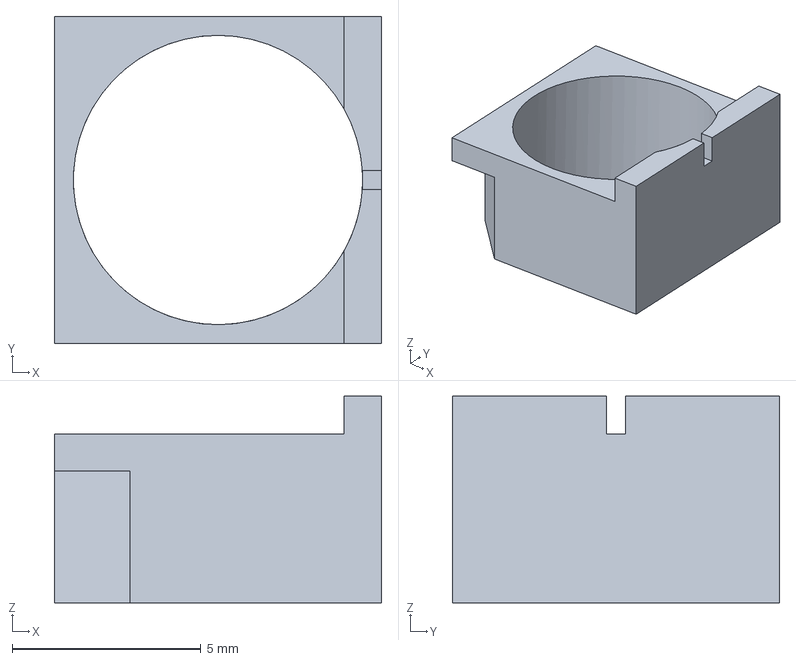
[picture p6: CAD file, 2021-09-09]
body_components/kiloscope/lower_subassembly.step
8.67 x 8.67 x 5.48 mm

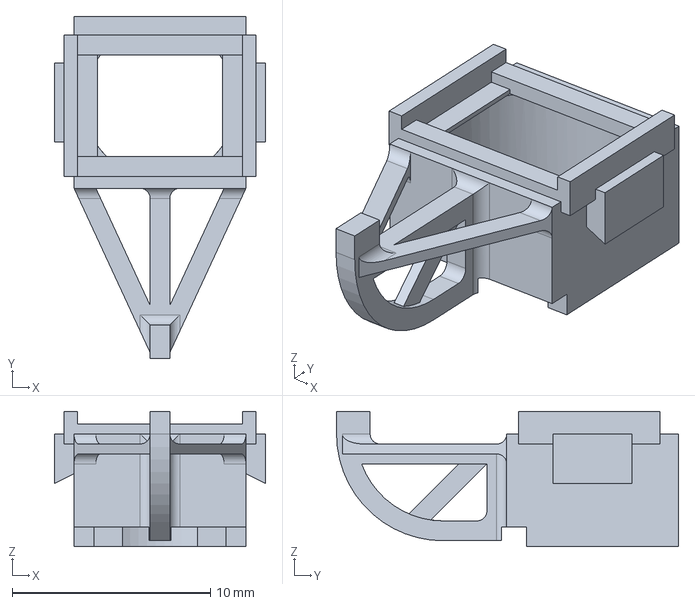
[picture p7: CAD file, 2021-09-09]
body_components/kiloscope/upper_subassembly.step
10.7 x 17.3 x 6.83 mm

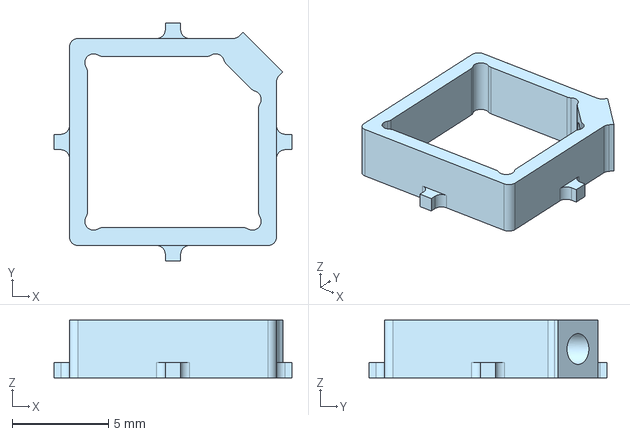
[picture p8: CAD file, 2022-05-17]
body_components/kiloscope/baseplate.step
12.3 x 12.3 x 3.00 mm

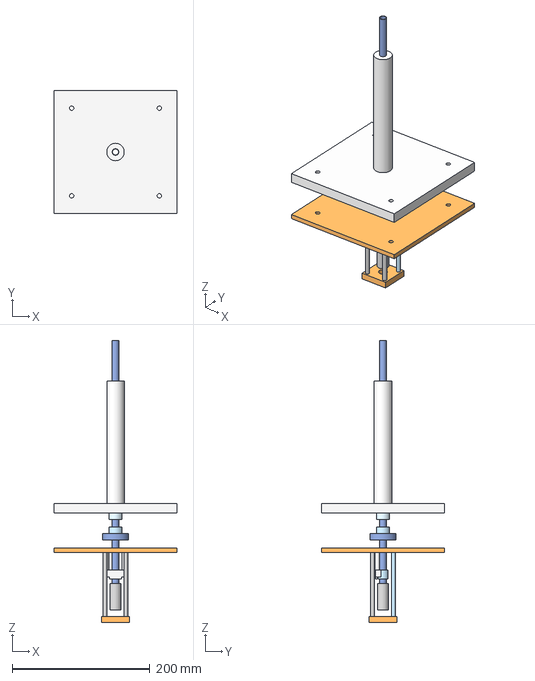
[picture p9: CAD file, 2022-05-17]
commutator/commutator.step
177.8 x 177.8 x 408.8 mm

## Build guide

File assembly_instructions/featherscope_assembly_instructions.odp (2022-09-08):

## Featherscope assembly

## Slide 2

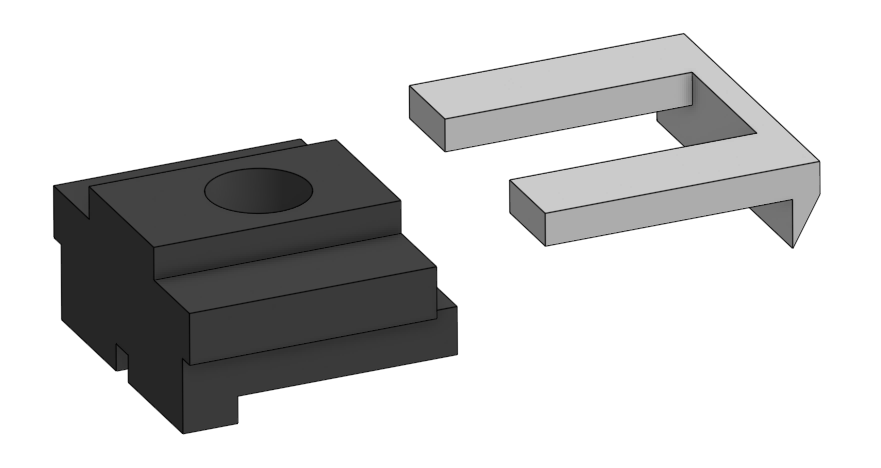
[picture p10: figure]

Slide magnetic bracket onto lower body

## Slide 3

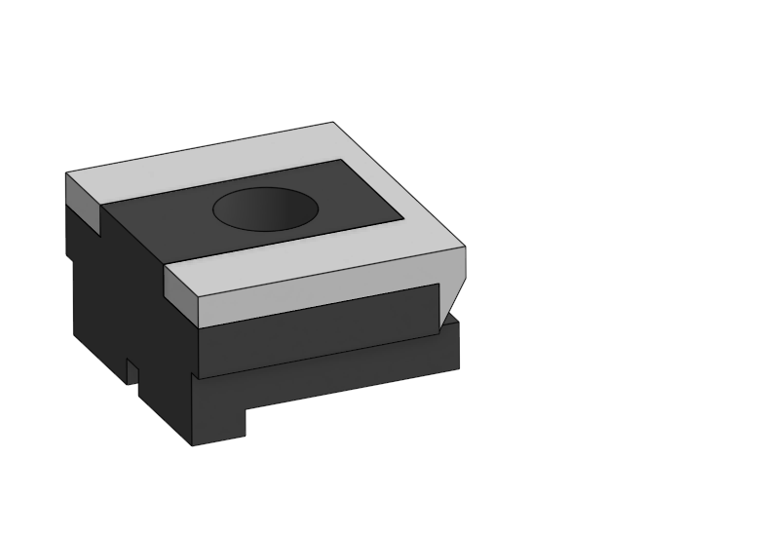
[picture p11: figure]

Apply cyanoacrylate glue to interface

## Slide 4

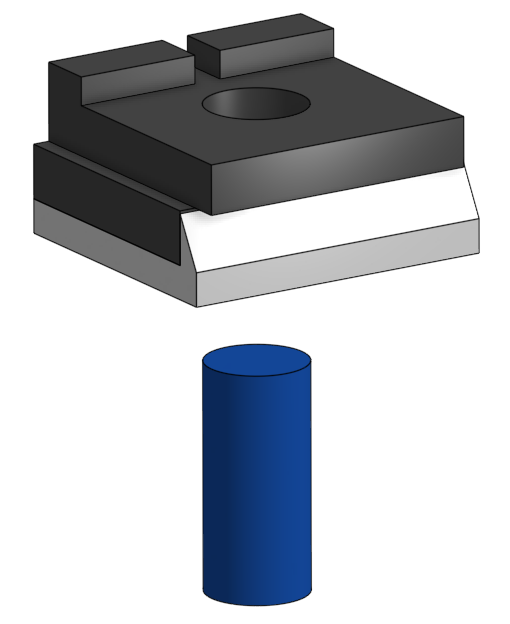
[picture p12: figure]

Insert objective lens into lower subassembly

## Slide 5

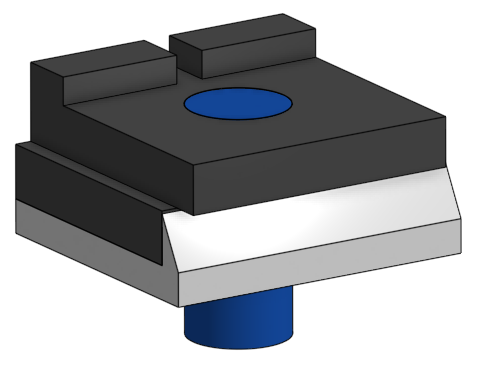
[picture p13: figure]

Push objective into body until top faces of lens and body are flush

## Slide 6

Apply 61 cement around interface

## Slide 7

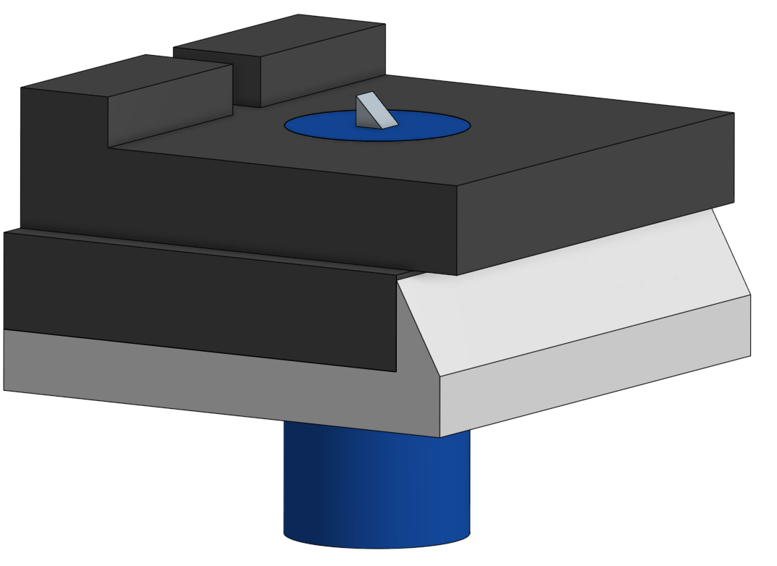
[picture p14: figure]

Attach prism with small amount of 61 cement

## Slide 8

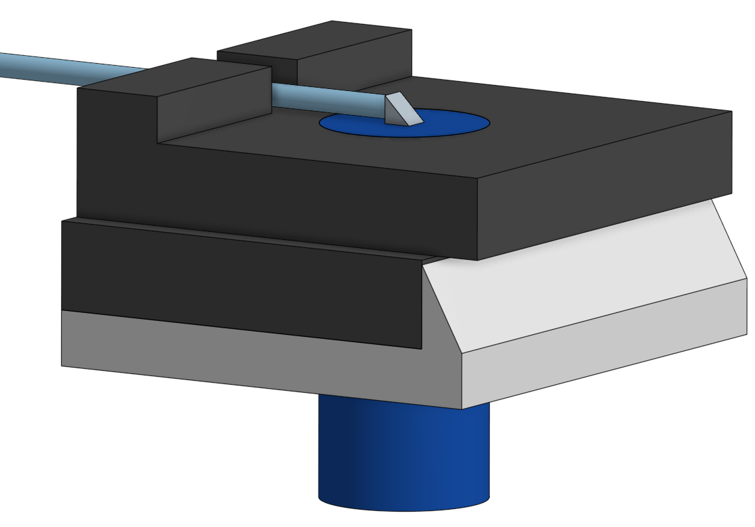
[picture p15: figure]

Insert fiber and attach fiber face to prism with small amount of 61 cement

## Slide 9

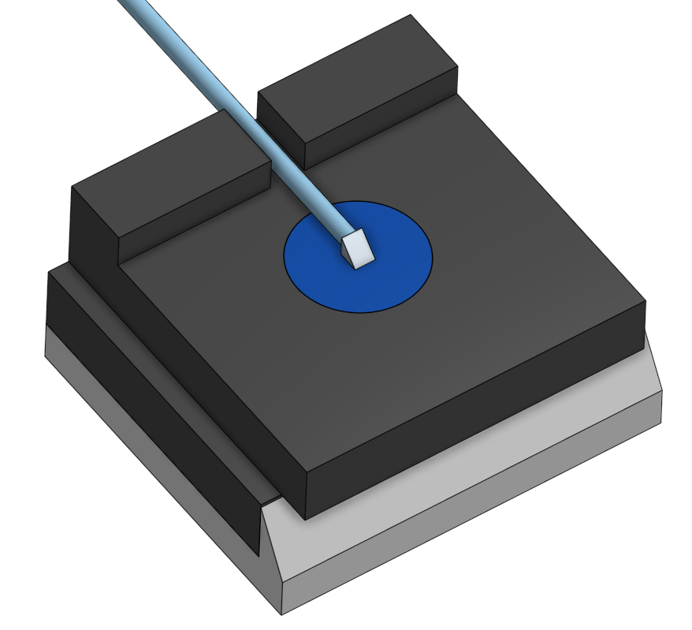
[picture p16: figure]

Secure fiber to body using 63 cement applied to notch

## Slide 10

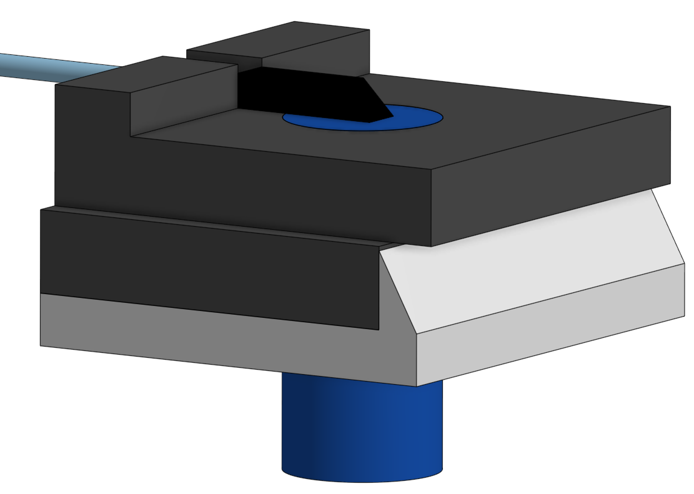
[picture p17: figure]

Cover prism-fiber assembly using nail polish

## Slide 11

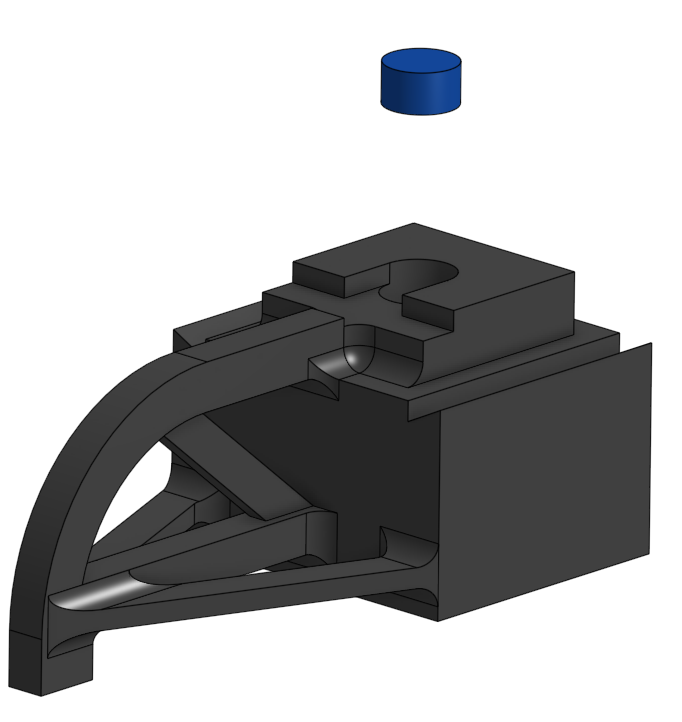
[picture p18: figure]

Insert tube lens into body

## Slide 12

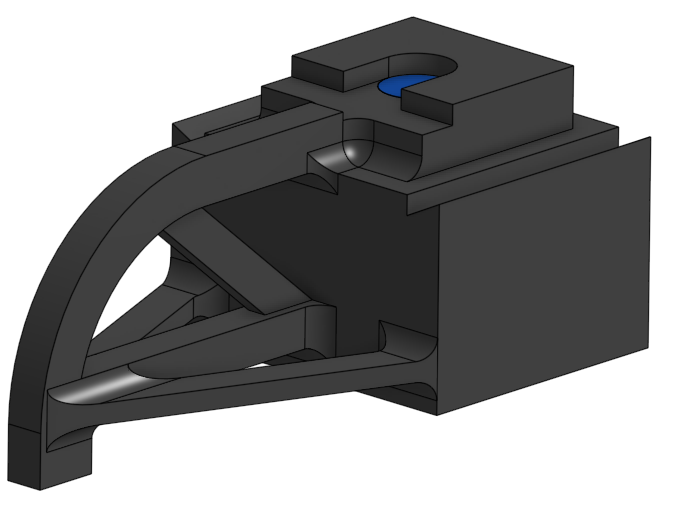
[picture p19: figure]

Push tube lens until faces of lens and body are flush

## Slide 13

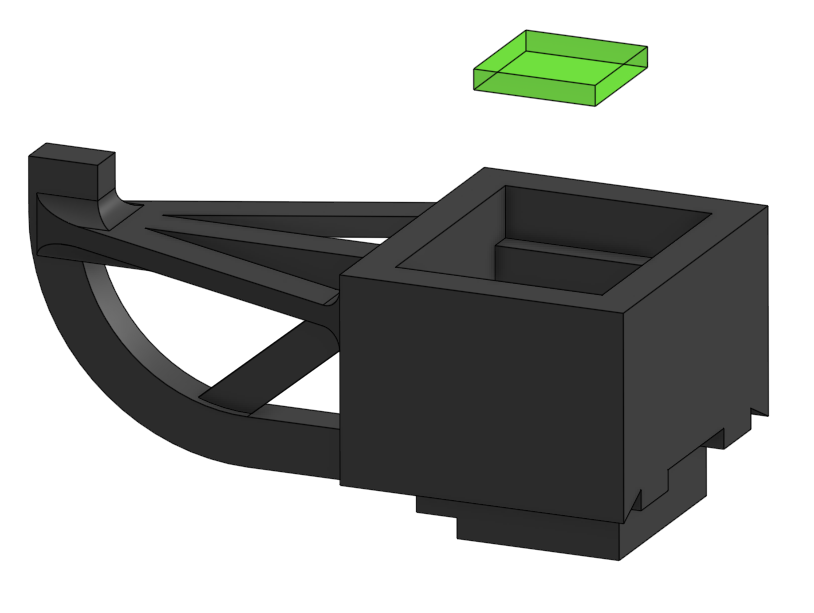
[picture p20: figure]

Insert dielectric filter

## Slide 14

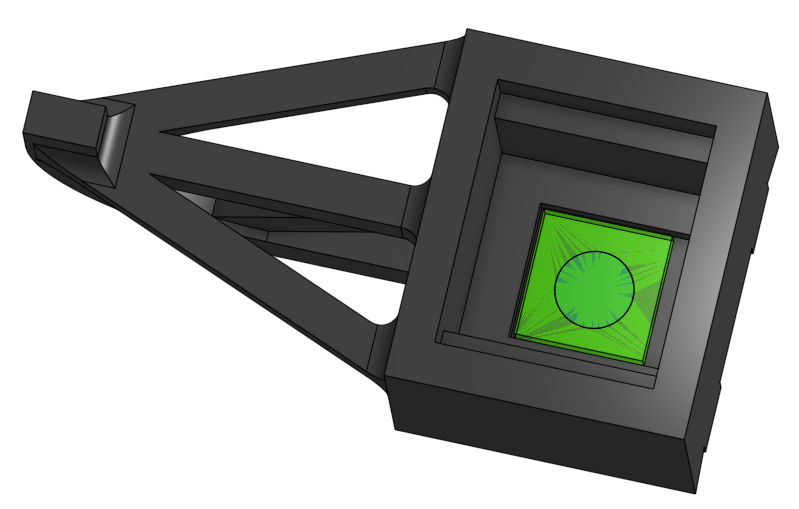
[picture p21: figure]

Attach filter using 61 cement applied between filter and lens

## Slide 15

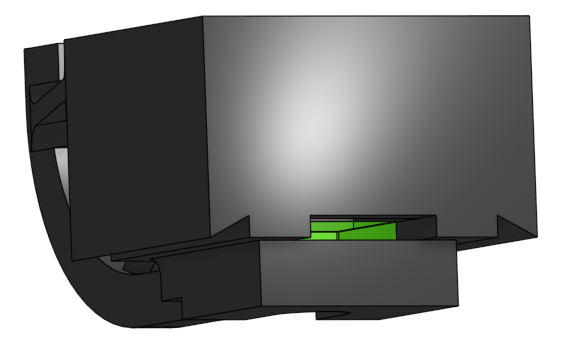
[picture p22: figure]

Cure cement using window on side of body

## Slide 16

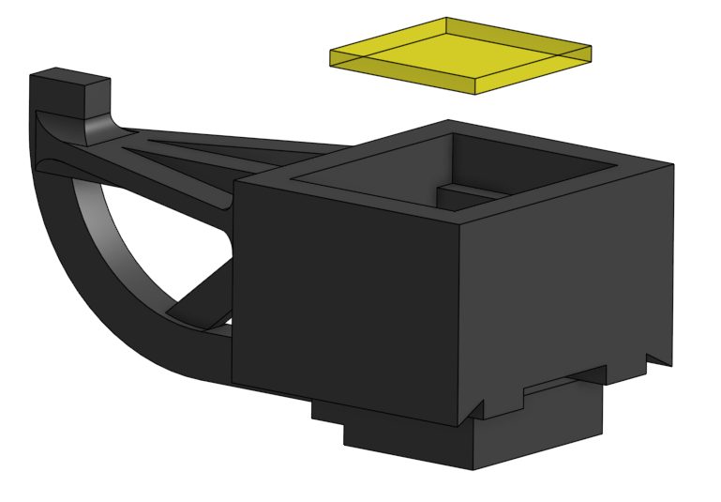
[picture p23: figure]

Insert wratten filter

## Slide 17

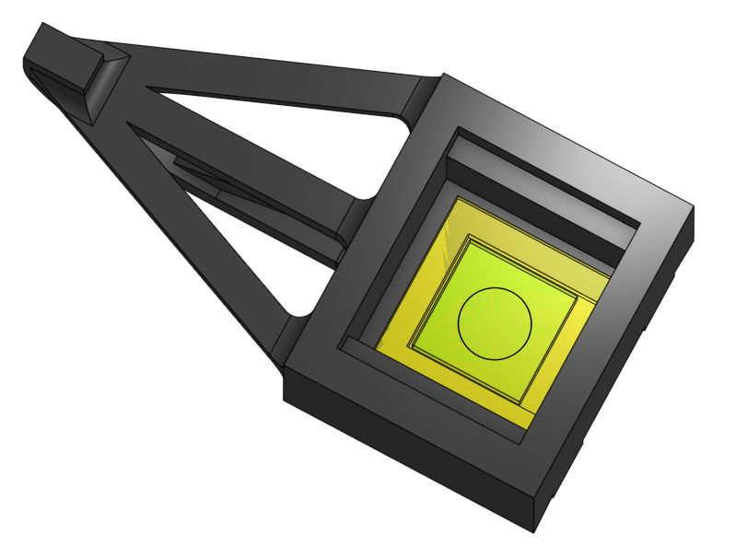
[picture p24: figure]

Attach using 61 cement between filters and cure using window

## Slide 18

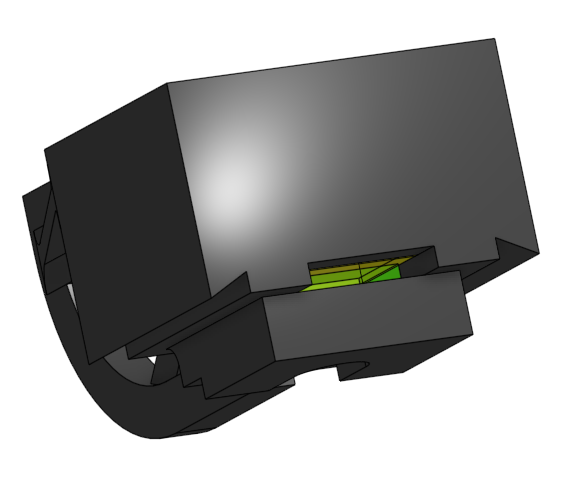
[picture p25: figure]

Seal window using nail polish

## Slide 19

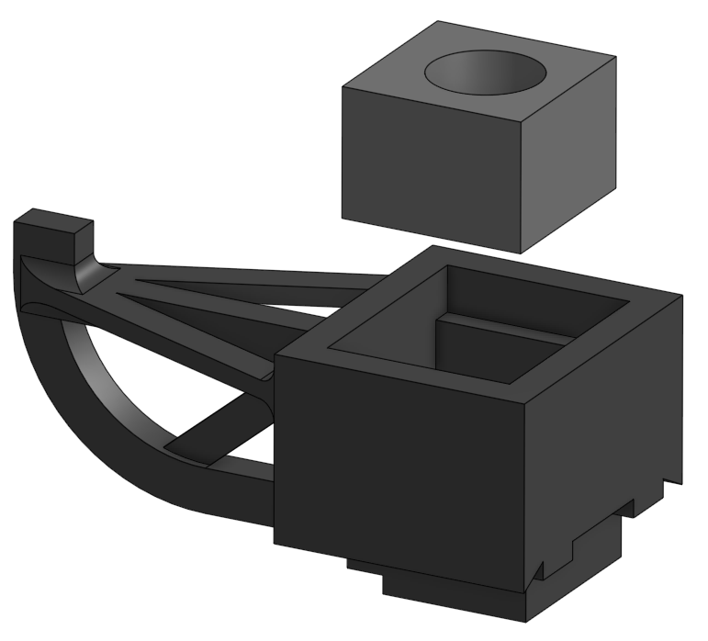
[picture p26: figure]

Insert focus spring into body

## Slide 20

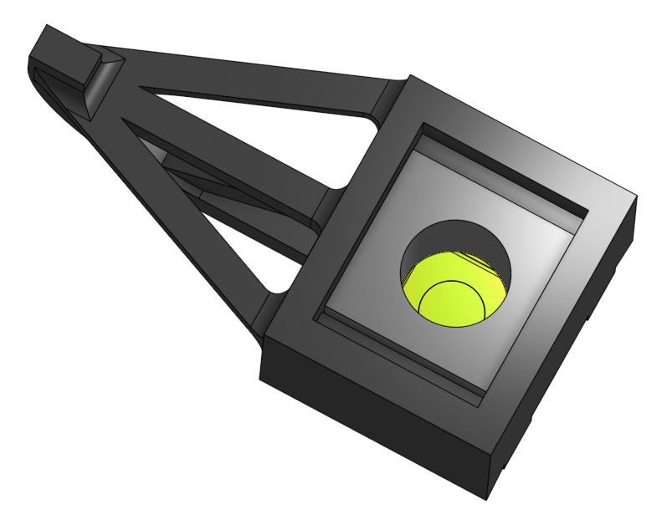
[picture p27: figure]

After insertion

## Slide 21

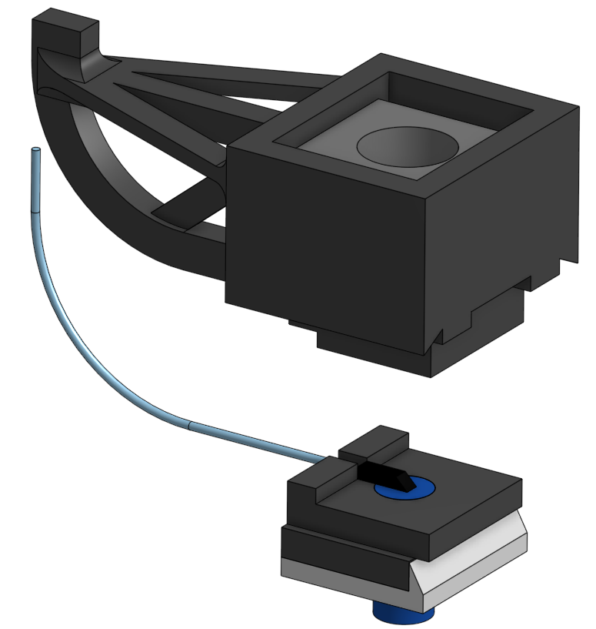
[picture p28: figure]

Align subassemblies

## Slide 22

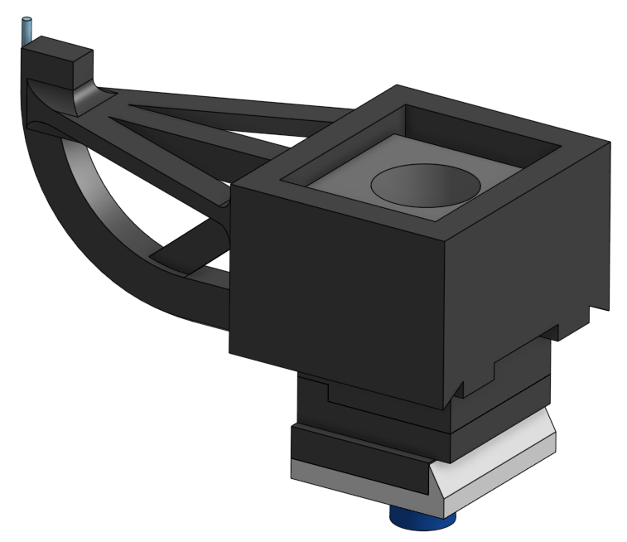
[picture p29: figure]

Attach subassemblies using 63 cement applied to interface

Attach fiber to relief arm using 5 minute epoxy

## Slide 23

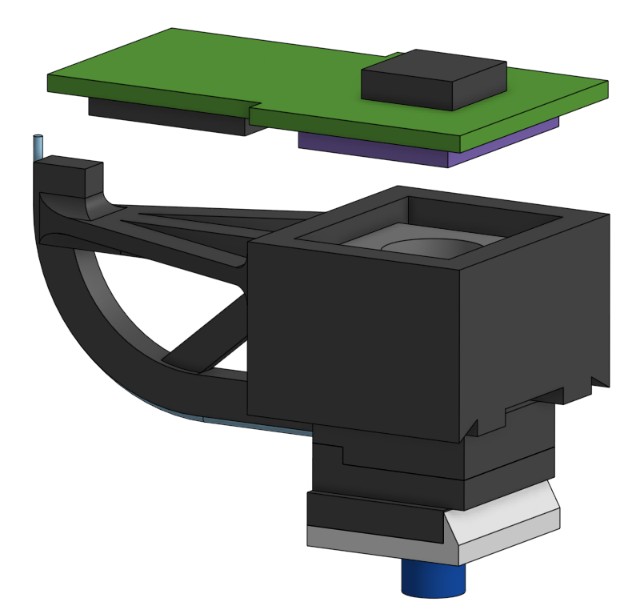
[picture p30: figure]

Insert PCB into body

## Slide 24

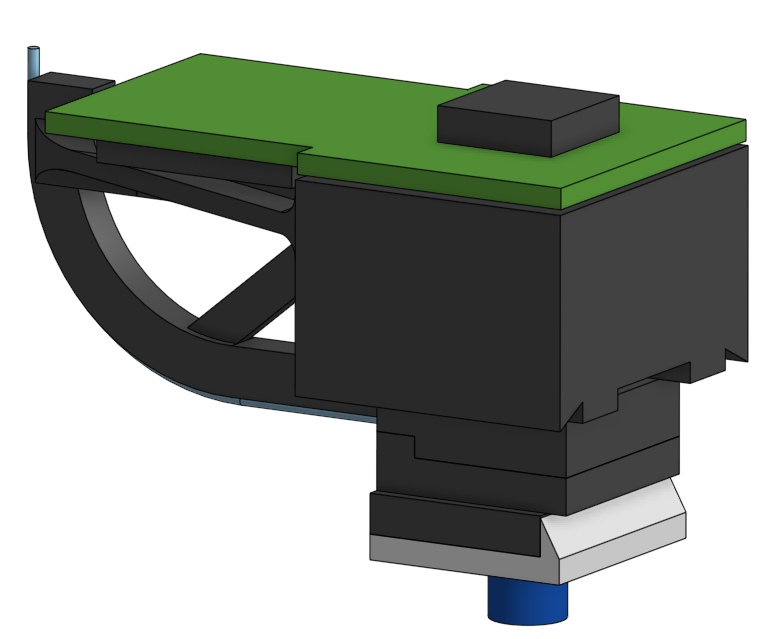
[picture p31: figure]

After installation

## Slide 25

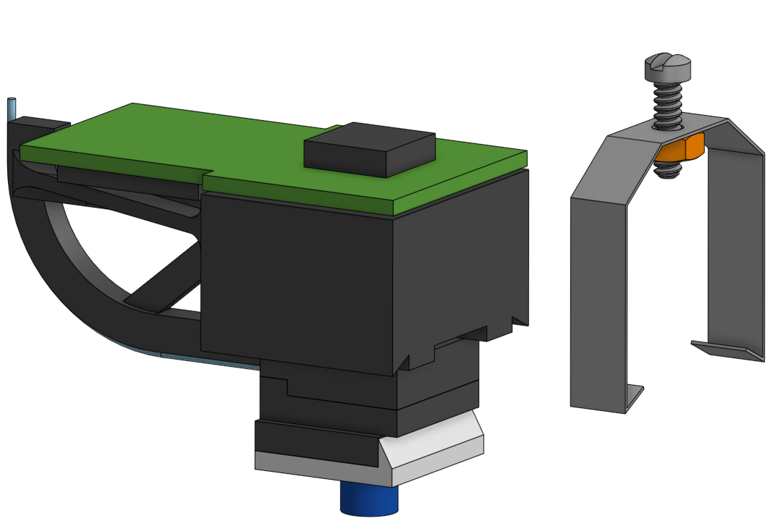
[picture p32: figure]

Slide focus bracket onto body

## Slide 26

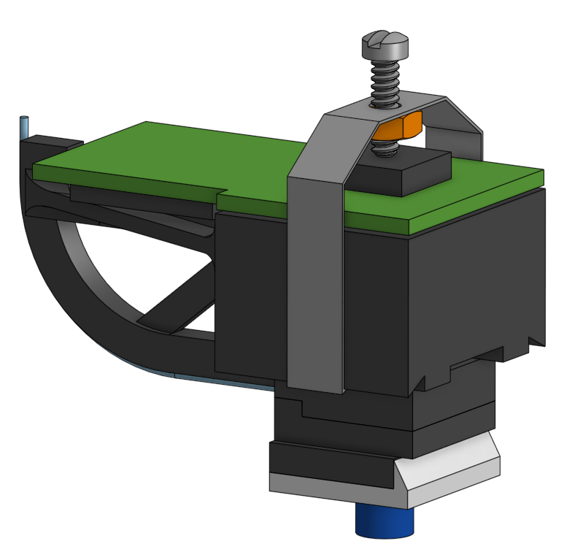
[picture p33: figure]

Assembly complete

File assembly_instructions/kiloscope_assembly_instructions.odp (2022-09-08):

## Kiloscope assembly

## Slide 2

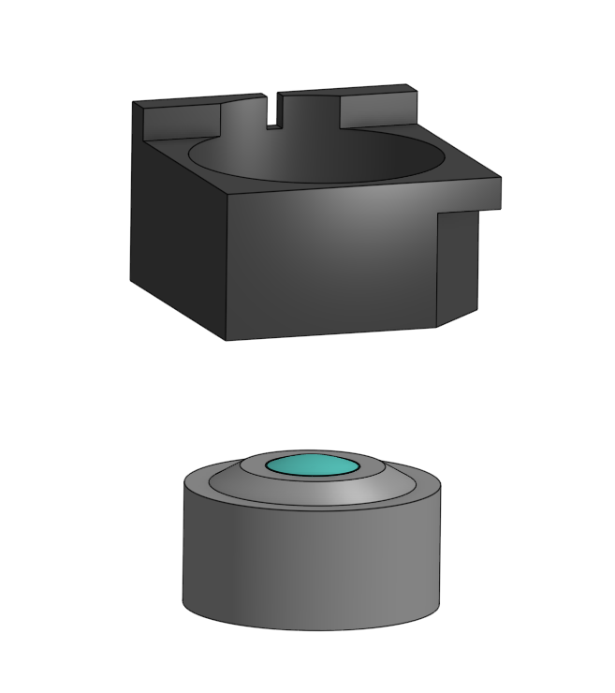
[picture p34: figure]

Ream the hole in the lower subassembly. Insert objective lens into lower subassembly

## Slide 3

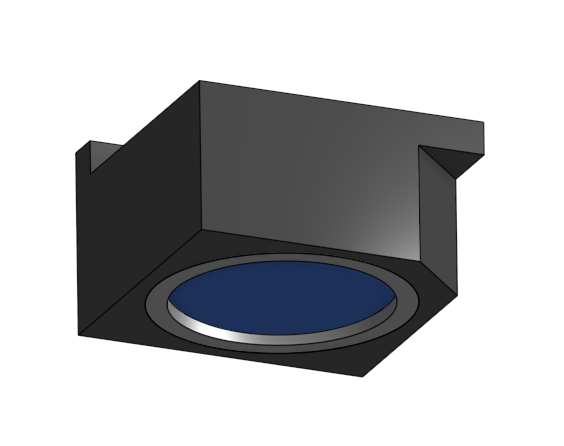
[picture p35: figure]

Push lens until bottom faces are flush. Apply 61 cement along the circular interface between components

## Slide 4

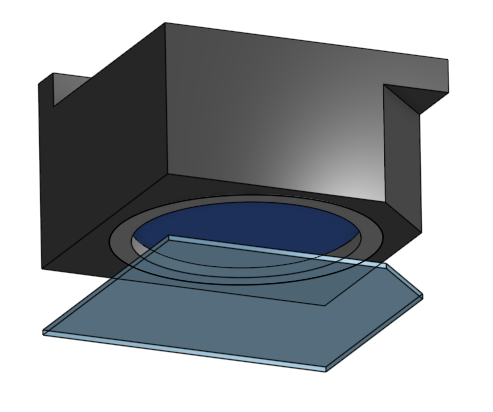
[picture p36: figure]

Align lower glass coverslip with lower subassembly

Ensure that coverslip does not hang over the sides of the plastic or you will not be able to seat the device in the head mount.

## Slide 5

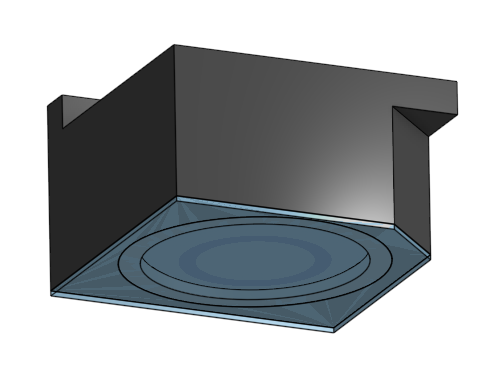
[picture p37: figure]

Apply 61 cement along the outside where the components meet

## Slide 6

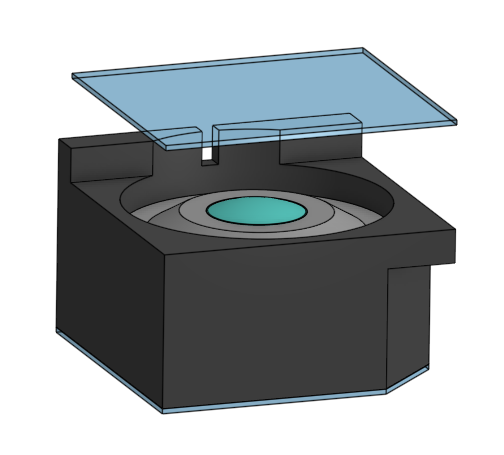
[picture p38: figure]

Align upper coverslip with subassembly

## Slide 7

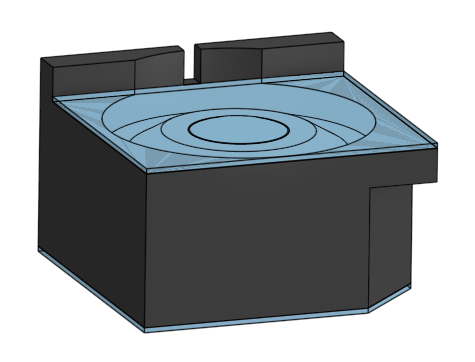
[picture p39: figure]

Apply 61 cement along the outside interface

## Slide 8

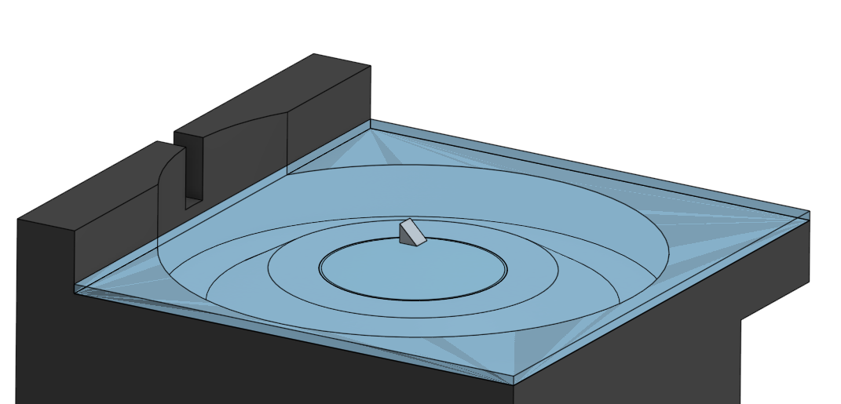
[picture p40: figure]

Align prism and attach with very small amount of 61 cement

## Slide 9

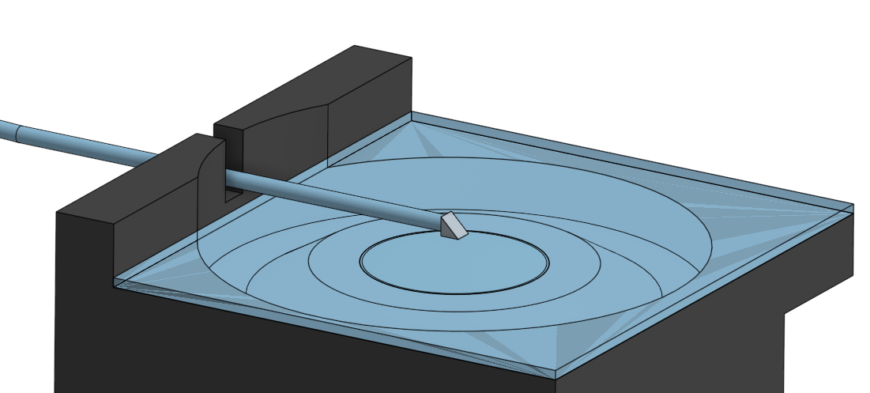
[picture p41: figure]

Align fiber and attach with 61 cement between fiber face and prism

Secure fiber to body using 63 cement applied to notch

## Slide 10

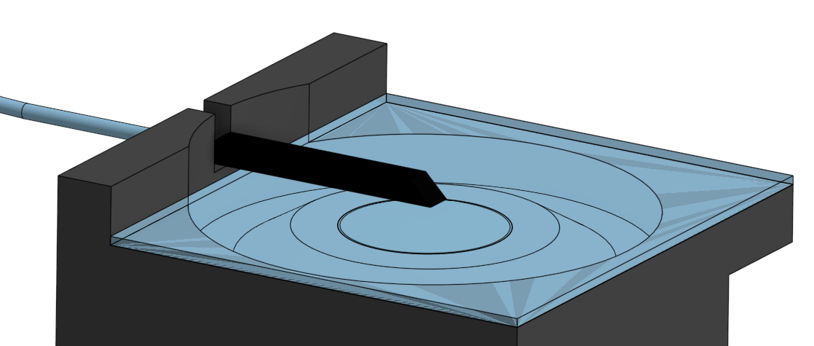
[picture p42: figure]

Apply nail polish to prism-fiber assembly

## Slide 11

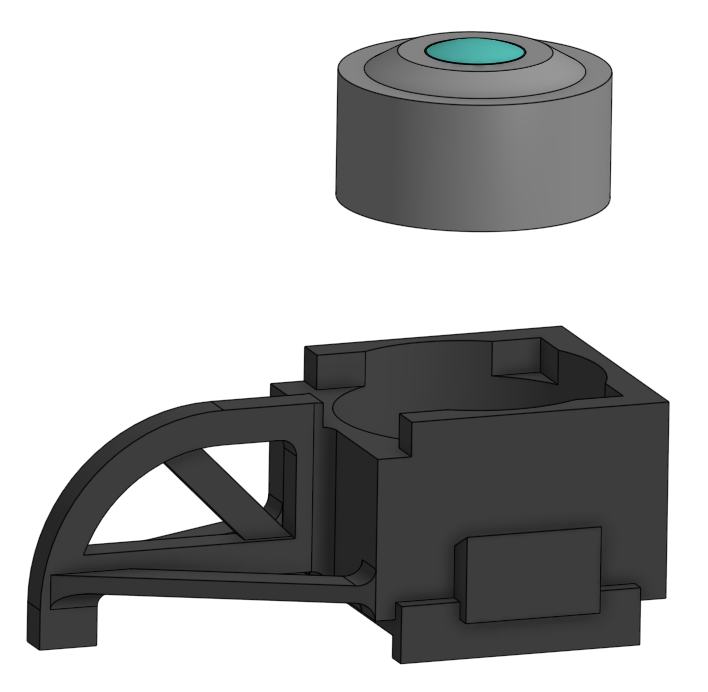
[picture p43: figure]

Ream the hole in the upper assembly being careful not to punch through the top lens stops.

Insert tube lens into upper subassembly

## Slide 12

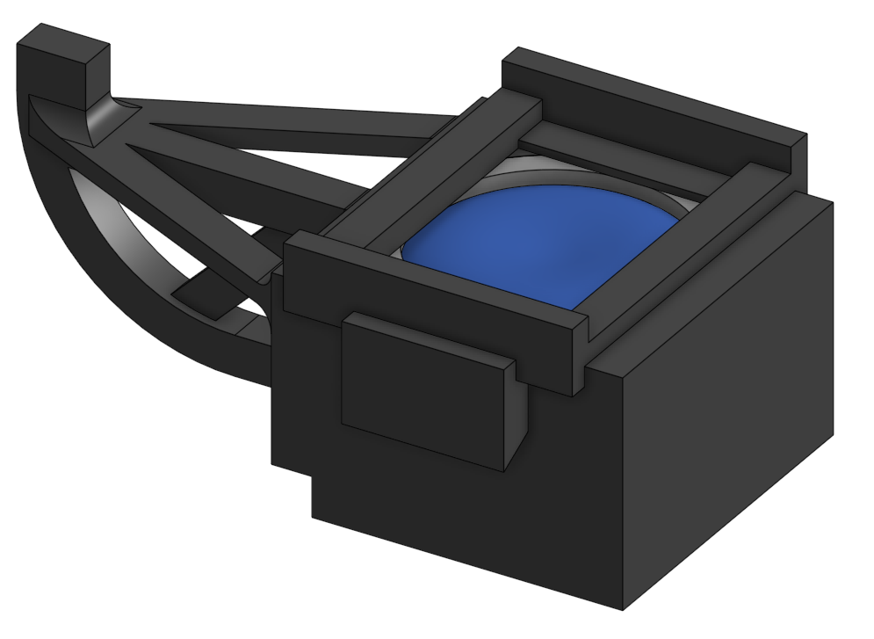
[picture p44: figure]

Ensure edge of lens assembly is flush with inner lip

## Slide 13

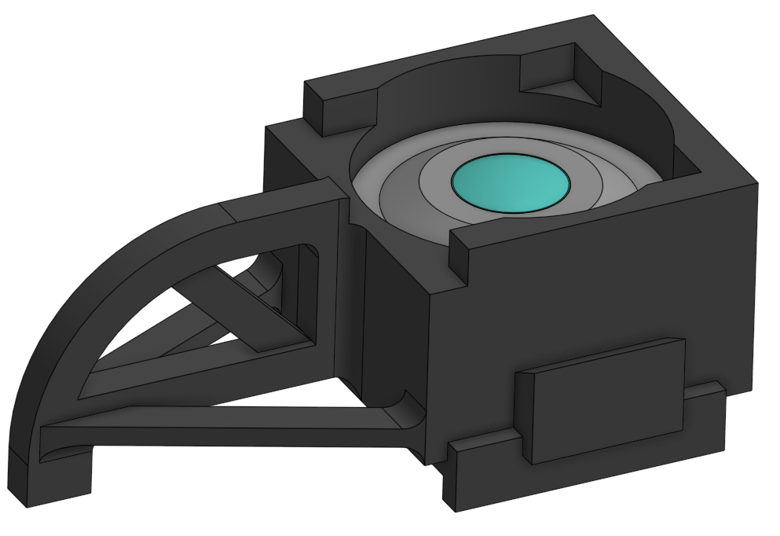
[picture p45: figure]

Apply 63 cement to interface

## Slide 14

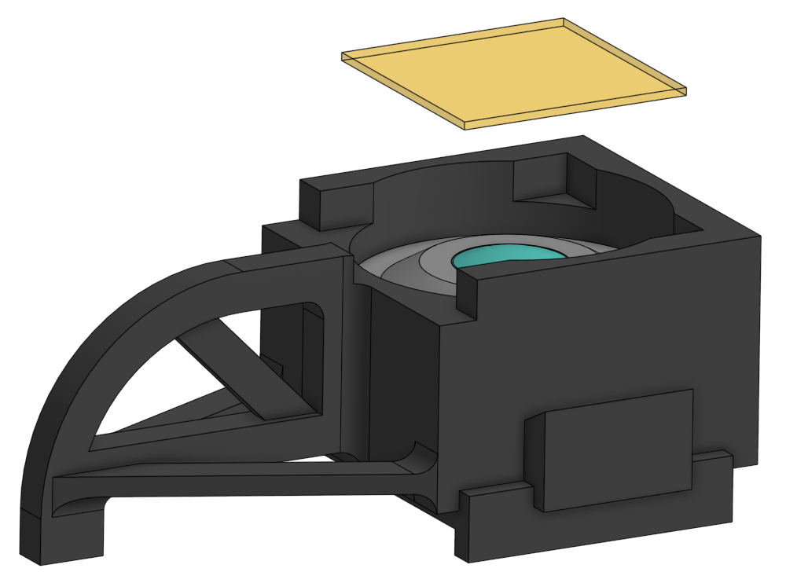
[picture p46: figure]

Cut wratten filter from large sheet. Align wratten filter with body

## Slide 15

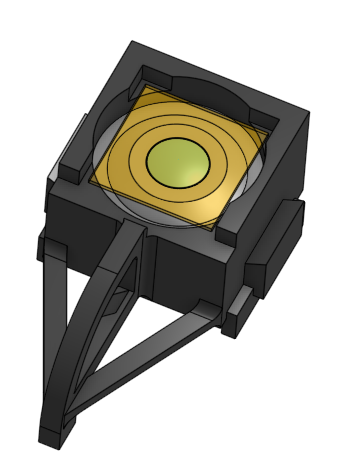
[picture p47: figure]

Apply 63 cement to corners

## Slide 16

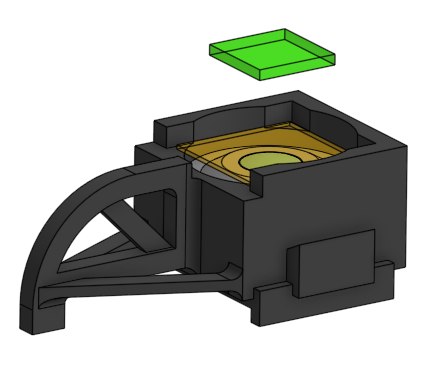
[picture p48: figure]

Align dielectric filter with lens aperture. The coating should face away from the wratten filter. Adhere with 61 cement

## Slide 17

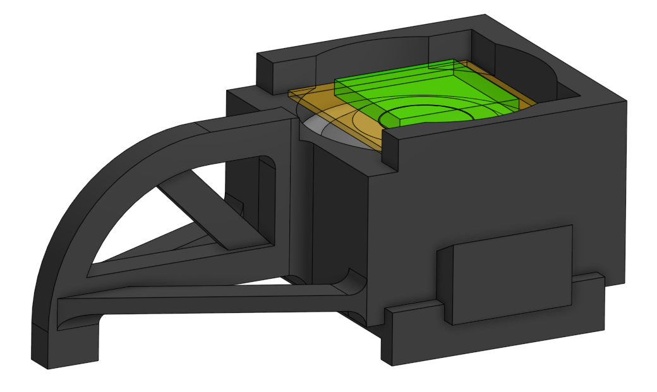
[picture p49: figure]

After installation

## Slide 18


Align the upper and lower subassemblies

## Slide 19


Apply 63 cement along the entire length of the interface between subassemblies

Cover fiber-support interface with 5 minute epoxy

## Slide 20


Align PCB with body

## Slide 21


After installation

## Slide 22


Slide focus bracket onto side ledges

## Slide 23


Assembly complete

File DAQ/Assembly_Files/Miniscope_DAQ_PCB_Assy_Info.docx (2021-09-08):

Miniscope DAQ PCB Assembly Information

Assembly:

- 1 BGA (.8mm pitch)
- Through Hole:
  - Unique components: 5
  - Total parts: 7
  - All on top layer
- Surface Mount:
  - Unique components: 56
  - Smallest footprint: 0402
  - Total parts: 189
  - All on top layer
  - C67, C68, C72, C83 are unpolarized ceramic capacitors. Ignore polarization marks on board for these components.
  - U11, U12, U14 LED orientation is shown below:


Top of LED

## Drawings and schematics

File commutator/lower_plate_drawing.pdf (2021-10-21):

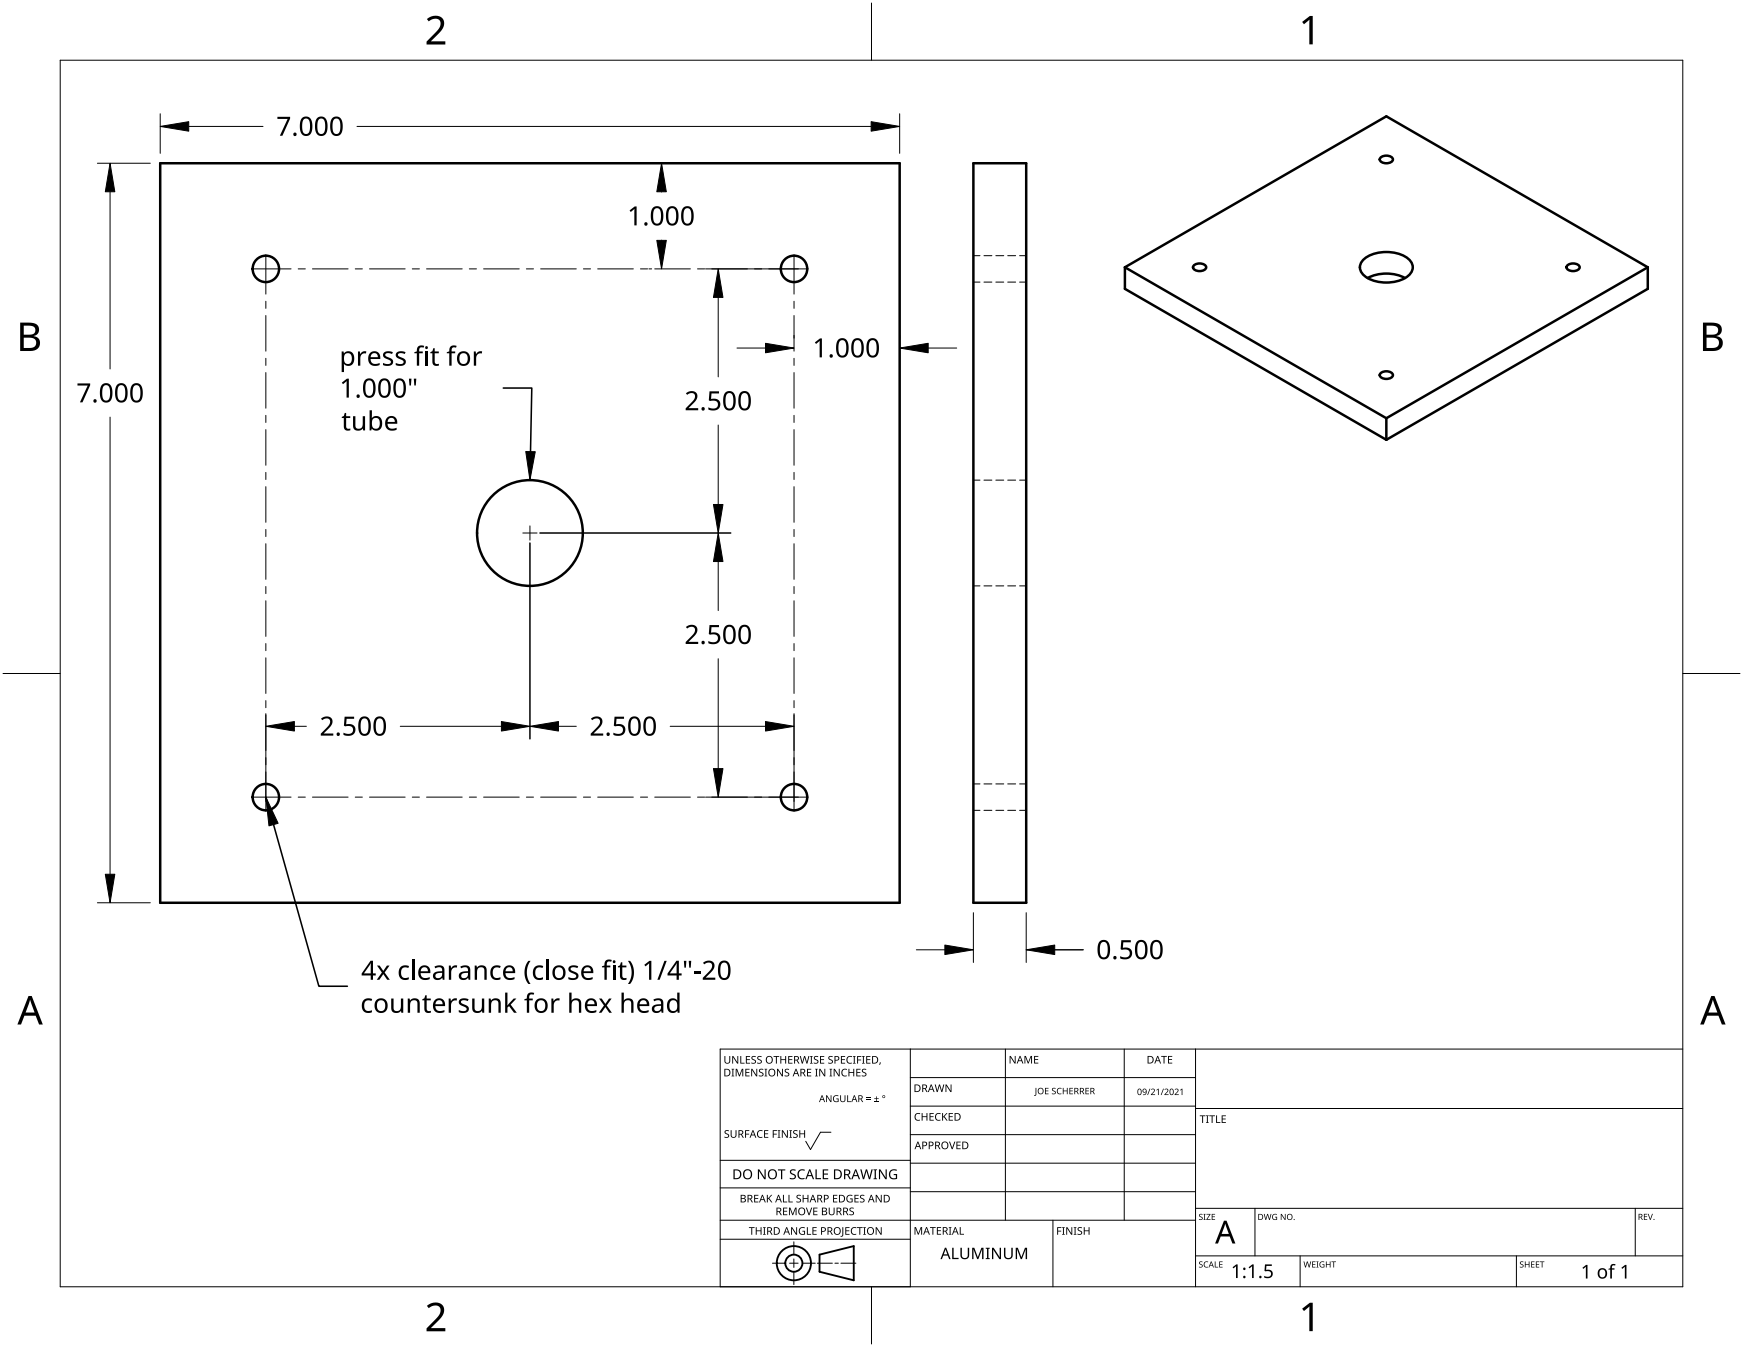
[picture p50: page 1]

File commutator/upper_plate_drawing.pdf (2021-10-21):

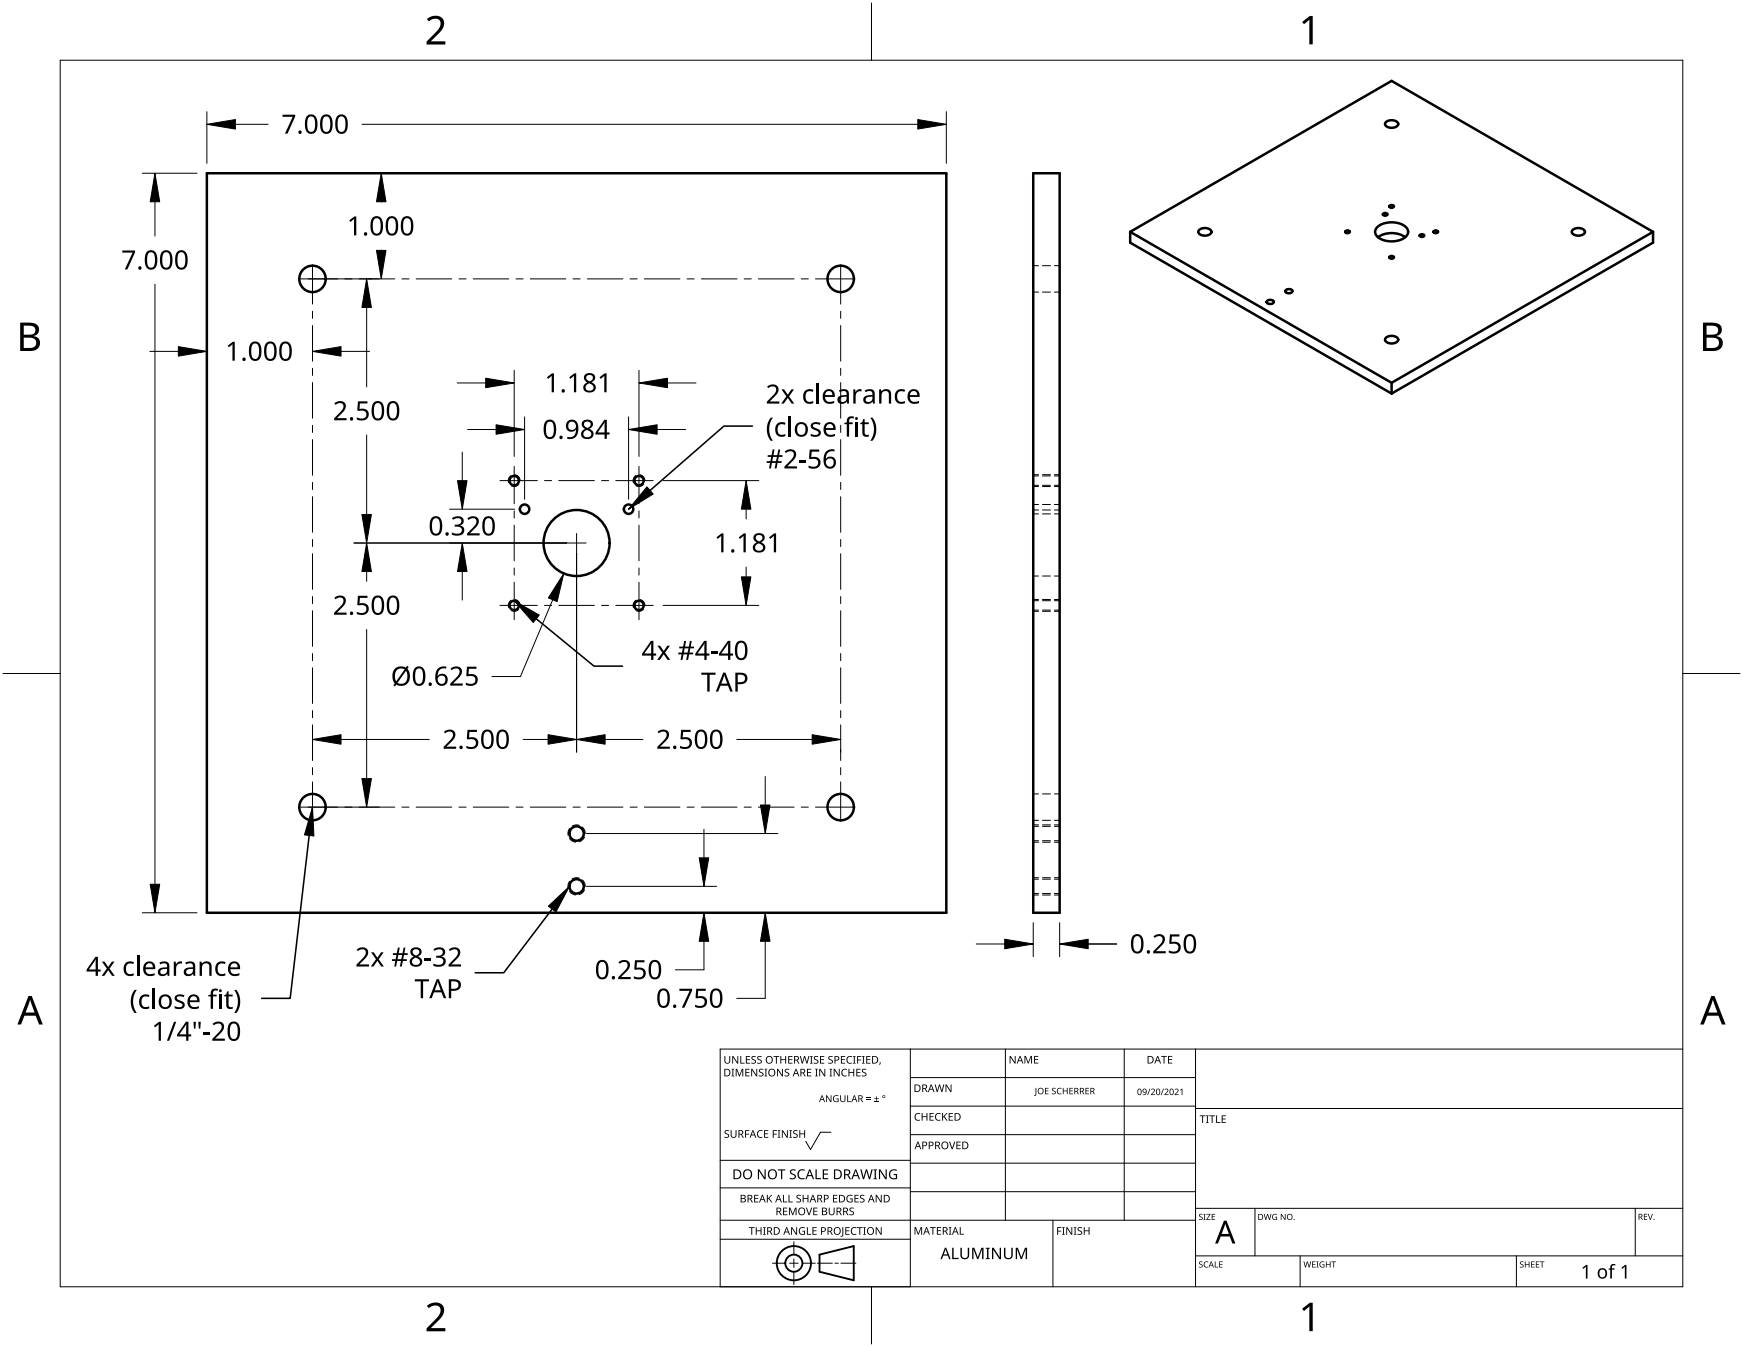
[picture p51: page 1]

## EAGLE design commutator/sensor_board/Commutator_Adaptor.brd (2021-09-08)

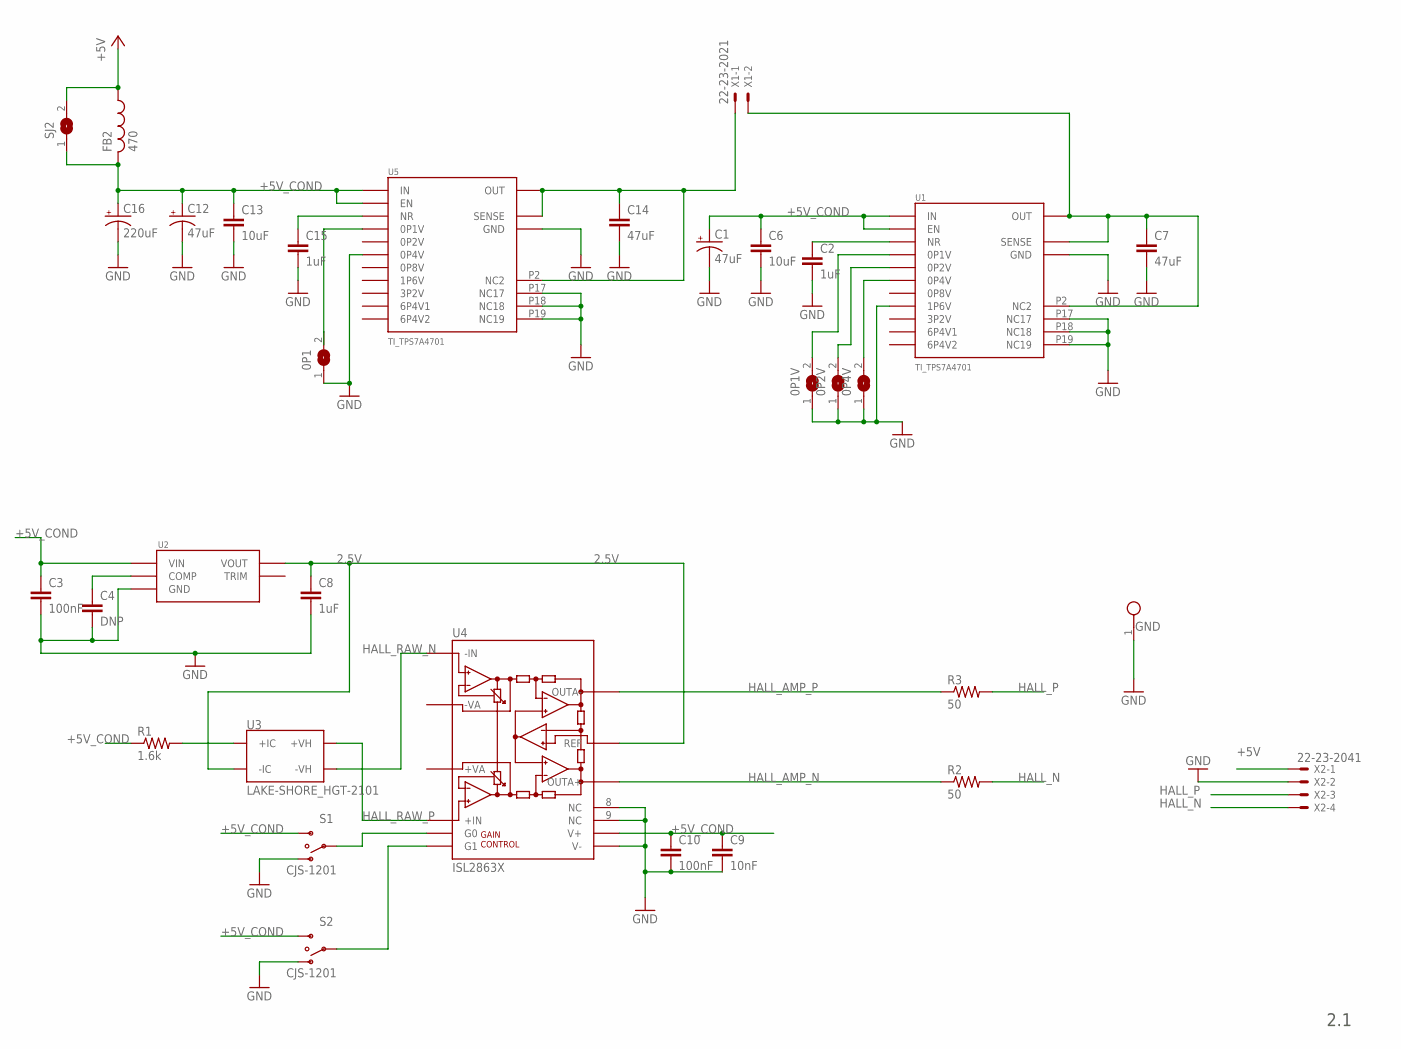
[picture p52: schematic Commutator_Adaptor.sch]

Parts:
0P1, 0P1V, 0P2V, 0P4V: SJ
C1, C12: 47uF; 1210POL
C2, C8, C15: 1uF; 0603
C3, C10: 100nF; 0402
C4: DNP; 0402
C6, C13: 10uF; 0805
C7, C14: 47uF; 1210
C9: 10nF; 0402
C16: 220uF; JA0
FB2: 470; 0603
GND: TESTPOINT_SMALL
R1: 1.6k; 0402
R2, R3: 50; 0402
S1, S2: CJS-1201; CJS-1201A1
SJ2: SJ
U1, U5: TI_TPS7A4701; 20-VQFN(5X5)
U2: ISL21090; SO08
U3: LAKE-SHORE_HGT-2101; HGT-2101-SIDE
U4: ISL2863X; TSSOP14
X1: 22-23-2021
X2: 22-23-2041

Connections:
1P8: C14.POS (1), U5.P1 (OUT), U5.P2 (NC2), U5.P3 (SENSE), U5.P20 (OUT), X1.1
2.5V: C8.1, U2.6 (VOUT), U3.PIN1 (-IC), U4.11 (REF)
3P3: C7.POS (1), U1.P1 (OUT), U1.P2 (NC2), U1.P3 (SENSE), U1.P20 (OUT), X1.2
+5V: FB2.1, SJ2.2, X2.1
+5V_COND: C1.POS (+), C3.1, C6.1, C9.1, C10.1, C12.POS (+), C13.1, C16.POS (+), FB2.2, R1.1, S1.P$3 (S), S2.P$3 (S), SJ2.1, U1.P13 (EN), U1.P15 (IN), U1.P16 (IN), U2.2 (VIN), U4.14 (V+), U5.P13 (EN), U5.P15 (IN), U5.P16 (IN)
GND: 0P1.1, 0P1V.1, 0P2V.1, 0P4V.1, C1.NEG (-), C2.2, C3.2, C4.2, C6.2, C7.NEG (2), C8.2, C9.2, C10.2, C12.NEG (-), C13.2, C14.NEG (2), C15.2, C16.NEG (-), GND.1, S1.P$1 (O), S2.P$1 (O), U1.P7 (GND), U1.P8 (1P6V), U1.P17 (NC17), U1.P18 (NC18), U1.P19 (NC19), U1.THERMAL@1 (GND), U1.THERMAL@2 (GND), U1.THERMAL@3 (GND), U1.THERMAL@4 (GND), U1.THERMAL@5 (GND), U1.THERMAL@6 (GND), U1.THERMAL@7 (GND), U1.THERMAL@8 (GND), U1.THERMAL@9 (GND), U1.THERMAL@10 (GND), U2.4 (GND), U4.7 (V-), U4.8 (NC), U4.9 (NC), U5.P7 (GND), U5.P10 (0P4V), U5.P17 (NC17), U5.P18 (NC18), U5.P19 (NC19), U5.THERMAL@1 (GND), U5.THERMAL@2 (GND), U5.THERMAL@3 (GND), U5.THERMAL@4 (GND), U5.THERMAL@5 (GND), U5.THERMAL@6 (GND), U5.THERMAL@7 (GND), U5.THERMAL@8 (GND), U5.THERMAL@9 (GND), U5.THERMAL@10 (GND), X2.2
HALL_AMP_N: R2.1, U4.12 (OUTA+)
HALL_AMP_P: R3.1, U4.10 (OUTA-)
HALL_N: R2.2, X2.4
HALL_P: R3.2, X2.3
HALL_RAW_N: U3.WIRE1 (-VH), U4.5 (-IN)
HALL_RAW_P: U3.PIN2 (+VH), U4.4 (+IN)
I_HALL: R1.2, U3.WIRE2 (+IC)
unnamed: C4.1, U2.3 (COMP)
unnamed: S1.P$2, U4.1 (G0)
unnamed: C15.1, U5.P14 (NR)
unnamed: S2.P$2, U4.2 (G1)
unnamed: 0P4V.2, U1.P10 (0P4V)
unnamed: C2.1, U1.P14 (NR)
unnamed: 0P2V.2, U1.P11 (0P2V)
unnamed: 0P1.2, U5.P12 (0P1V)
unnamed: 0P1V.2, U1.P12 (0P1V)

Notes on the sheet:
2.1

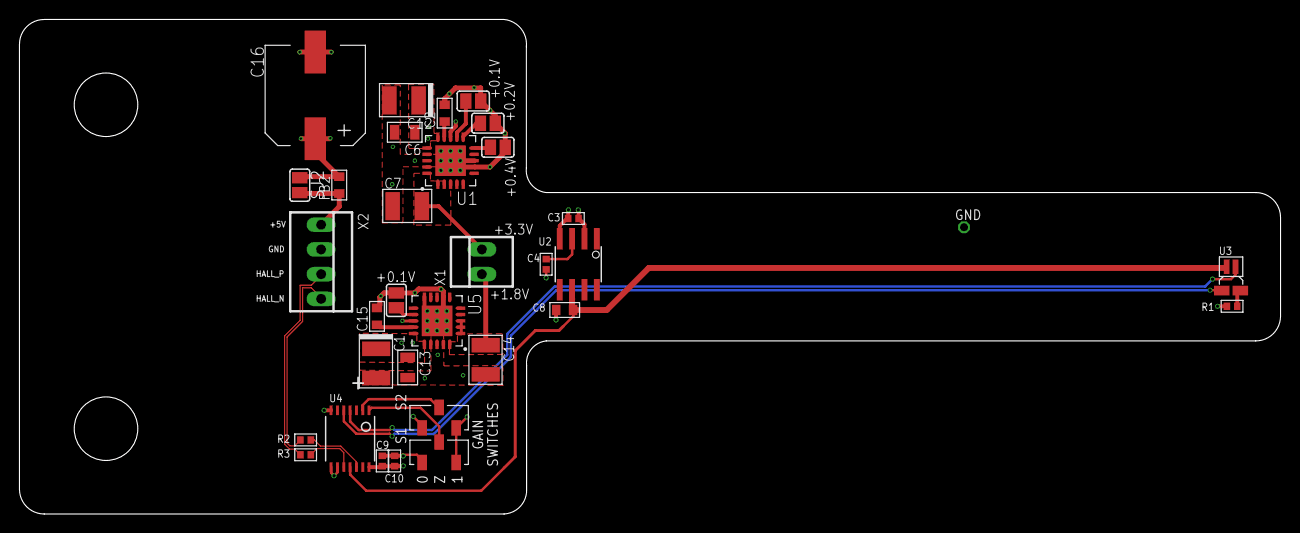
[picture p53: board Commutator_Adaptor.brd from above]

Board: 4 copper layers, 129.5 x 50.8 mm, 33 parts (0 on the bottom side), 22 nets.

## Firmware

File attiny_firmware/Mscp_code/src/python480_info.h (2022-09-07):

#ifndef PYHTON480_INFO_H
#define PYHTON480_INFO_H

// Sensor Registers:
// =================
#define SENSOR_REG_CHIP_ID               0
#define SENSOR_REG_CHIP_INFO             1
#define SENSOR_REG_CHIP_CONFIG           2
#define SENSOR_REG_SOFT_RESET_PLL        8
#define SENSOR_REG_SOFT_RESET_CGEN       9
#define SENSOR_REG_SOFT_RESET_ANALOG    10
#define SENSOR_REG_PLL_CONFIG           16
#define SENSOR_REG_IO_CONFIG            20
#define SENSOR_REG_PLL_LOCK             24
#define SENSOR_REG_CLOCK_CONFIG         32
#define SENSOR_REG_CLOCK_ENABLE         34
#define SENSOR_REG_IMAGE_CORE_CONFIG1   40
#define SENSOR_REG_IMAGE_CORE_CONFIG2   41
#define SENSOR_REG_AFE_CONFIG           48
#define SENSOR_REG_BIAS_PWR_CONFIG      64
#define SENSOR_REG_BIAS_CONFIG          65
#define SENSOR_REG_AFE_BIAS_CONFIG      66
#define SENSOR_REG_COLUMN_BIAS_CONFIG   67
#define SENSOR_REG_LVDS_BIAS_CONFIG     68
#define SENSOR_REG_ADC_BIAS             69
#define SENSOR_REG_CHARGE_PUMP_CONFIG   72
#define SENSOR_REG_TEMP_SENSOR_CONFIG   96
#define SENSOR_REG_TEMP_SENSOR_STATUS   97
#define SENSOR_REG_LVDS_CONFIG         112
#define SENSOR_REG_BLACK_CAL           128
#define SENSOR_REG_TEST_PAT_CONFIG     144
#define SENSOR_REG_TEST_PAT_0_1        146
#define SENSOR_REG_TEST_PAT_2_3        147
#define SENSOR_REG_TEST_PAT_CONFIG     144
#define SENSOR_REG_TEST_PAT_LSB_01     146
#define SENSOR_REG_TEST_PAT_LSB_23     147
#define SENSOR_REG_TEST_PAT_MSB_0123   150
#define SENSOR_REG_AEC_INTENSITY       161
#define SENSOR_REG_SEQ_GEN_CONFIG      192
#define SENSOR_REG_SEQ_DEL_CONFIG      193
#define SENSOR_REG_INTEGRATION_CONTROL 194
#define SENSOR_REG_ACTIVE_ROI          195
#define SENSOR_REG_BLACK_LINE_CONFIG   197
#define SENSOR_REG_MULT_TIMER_0        199
#define SENSOR_REG_FR_RST_LENGTH       200
#define SENSOR_REG_EXPOSURE0           201
#define SENSOR_REG_ANALOG_GAIN         204
#define SENSOR_REG_DIGITAL_GAIN        205
#define SENSOR_REG_ROI0_X_CONFIG       256
#define SENSOR_REG_ROI0_Y_START        257
#define SENSOR_REG_ROI0_Y_END          258
#define SENSOR_REG_ROI1_X_CONFIG       259
#define SENSOR_REG_ROI1_Y_START        260
#define SENSOR_REG_ROI1_Y_END          261
#define SENSOR_REG_ROI2_X_CONFIG       262
#define SENSOR_REG_ROI2_Y_START        263
#define SENSOR_REG_ROI2_Y_END          264
#define SENSOR_REG_ROI3_X_CONFIG       265
#define SENSOR_REG_ROI3_Y_START        266
#define SENSOR_REG_ROI3_Y_END          267

// Other info:
// ===========
#define SENSOR_NUM_ROIS                  4
#define SENSOR_PYTHON_480_WIDTH        808
#define SENSOR_PYTHON_480_HEIGHT       608
#define SENSOR_FR_LEN_480             8030

#endif

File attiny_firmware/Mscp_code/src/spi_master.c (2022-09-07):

#include "spi_master.h"

#include <stdint.h>

#include <avr/interrupt.h>
#include <util/delay.h>
#include <util/atomic.h>

#include "twi_slave.h"
#include "sensor_power_sequencing.h"

/*************
 * CONSTANTS *
 *************/

#define SPI_VPORT VPORTC
#define SPI_PORT  PORTC

#define SCK_bm    PIN0_bm
#define SCK_bp    PIN0_bp
#define SCKCTRL   PIN0CTRL
#define MOSI_bm   PIN2_bm
#define MOSI_bp   PIN2_bp
#define MOSICTRL  PIN2CTRL
#define MISO_bm   PIN1_bm
#define MISO_bp   PIN1_bp
#define MISOCTRL  PIN1CTRL
#define SSN_bm    PIN3_bm
#define SSN_bp    PIN3_bp
#define SSNCTRL   PIN3CTRL

#define SPI_STATE_PERIOD_US 1
#define SPI_CYCLE_PERIOD_US ( 2 * SPI_STATE_PERIOD_US )

/*******************
 * GLOBAL VARIABLES *
 ********************/

static spi_mutex_t spi_lock;

/*************************
 * FUNCTION DECLARATIONS *
 *************************/

static void spi_python480_write_register_addr(uint16_t reg_addr, bool is_write);

/************************
 * FUNCTION DEFINITIONS *
 ************************/

void spi_stop_transaction(void)
{
    SPI_VPORT.OUT |= SSN_bm;
}

void spi_start_transaction(void)
{
    SPI_VPORT.OUT &= ~SSN_bm; // Set SS low
}

void spi_write(uint8_t byte_out, int ntransmit)
{
    int i;
    if (ntransmit > 0 && ntransmit <= 8) {
        byte_out <<= 8 - ntransmit; // Skip over unused bits
        for (i = ntransmit; i > 0; i--) {
            /* Set MOSI to the msb of this byte */
            SPI_VPORT.OUT = (VPORTC.OUT & ~MOSI_bm) |
                ((byte_out >> 7) << MOSI_bp );
            _delay_us(SPI_STATE_PERIOD_US);
            /* assert sck to latch data */
            SPI_VPORT.OUT |= SCK_bm;
            _delay_us(SPI_STATE_PERIOD_US);
            /* de-assert sck for next bit */
            SPI_VPORT.OUT &= ~SCK_bm;
            /* shift the byte */
            byte_out <<= 1;
        }
    }
}

void spi_write_word(uint16_t word_out, int ntransmit)
{
    if (ntransmit <= 16) {
        if (ntransmit > 8) {
            spi_write(word_out >> 8, ntransmit - 8);
            _delay_us(SPI_STATE_PERIOD_US);
            spi_write(word_out, 8);
        } else if (ntransmit > 0) {
            spi_write(word_out, ntransmit);
        }
    }
}

uint8_t spi_read(void) {
    uint8_t byte_in;
    int i;
    // PIN1 is SCK
    // PIN2 is MISO
    /* assert sck so slave sets up next bit */
    SPI_VPORT.OUT |= SCK_bm;
    _delay_us(SPI_STATE_PERIOD_US);
    byte_in = (SPI_VPORT.IN & MISO_bm) >> MISO_bp;
    /* de-assert sck for next bit */
    SPI_VPORT.OUT &= ~SCK_bm;
    for (i = 0; i < 7; i++) {
        /* assert sck so slave sets up next bit */
        _delay_us(SPI_STATE_PERIOD_US);
        SPI_VPORT.OUT |= SCK_bm;
        _delay_us(SPI_STATE_PERIOD_US);
        byte_in <<= 1;
        byte_in |= (SPI_VPORT.IN & MISO_bm) >> MISO_bp;
        /* de-assert sck for next bit */
        SPI_VPORT.OUT &= ~SCK_bm;
    }
    return byte_in;
}

uint16_t spi_read_word(void) {
    uint16_t word_in;
    word_in = spi_read() << 8; // MSB
    _delay_us(SPI_STATE_PERIOD_US);
    word_in |= spi_read(); // LSB
    return word_in;
}

spi_mutex_t current_spi_lock(void) {
    return spi_lock;
}

bool spi_trylock(spi_mutex_t requester)
{
    bool res = false;
    if (spi_lock == SPI_NO_LOCK) {
        switch (requester) {
        case SPI_TWI:
            sequencing_disable_interrupts();
            spi_lock = SPI_TWI;
            break;
        case SPI_MAIN:
            twi_disable_interrupts();
            spi_lock = SPI_MAIN;
            break;
        case SPI_NO_LOCK:
            break;
        }
        res = true;
    } else if (requester == spi_lock) {
        res = true;
    } else {
        res = false;
    }
    return res;
}

bool spi_trylock_atomic(spi_mutex_t requester) {
    bool res = false;
    ATOMIC_BLOCK(ATOMIC_RESTORESTATE)
    {
        res = spi_trylock(requester);
    }
    return res;
}

bool spi_tryunlock(spi_mutex_t requester) {
    bool res = false;
    if (requester == spi_lock) {
        switch(spi_lock) {
        case SPI_NO_LOCK:
            break;
        case SPI_TWI:
            sequencing_enable_interrupts();
            break;
        case SPI_MAIN:
            twi_enable_interrupts();
            break;
        }
        spi_lock = SPI_NO_LOCK;
        res = true;
    } else {
        res = false;
    }
    return res;
}

bool spi_tryunlock_atomic(spi_mutex_t requester) {
    bool res;
    ATOMIC_BLOCK(ATOMIC_RESTORESTATE)
    {
        res = spi_tryunlock(requester);
    }
    return res;
}

void spi_enable(void)
{
  SPI0.CTRLA |= SPI_ENABLE_bm;
}

void spi_disable(void)
{
  SPI0.CTRLA &= ~SPI_ENABLE_bm;
}

static void spi_python480_write_register_addr(uint16_t reg_addr, bool is_write)
{
    reg_addr <<= 1;
    reg_addr |= is_write;
    spi_write_word(reg_addr, 10);
}

/* Assumes 9 bit register address is at least significant position in reg_addr
 * Assumes spi is enabled and in mode 0 at time of call
 * Leaves spi enabled in mode 0
 */
void spi_python480_write(uint16_t reg_addr, uint16_t reg_value)
{
    spi_start_transaction();
    _delay_us(SPI_CYCLE_PERIOD_US);
    spi_python480_write_register_addr(reg_addr, true);
    _delay_us(SPI_STATE_PERIOD_US);
    spi_write_word(reg_value, 16);
    _delay_us(SPI_CYCLE_PERIOD_US);
    spi_stop_transaction();
    _delay_us(2 * SPI_CYCLE_PERIOD_US);
}

/* Assumes 9 bit register address is at least significant position in reg_addr
 * Assumes spi is enabled and in mode 0 at time of call
 * leaves SPI enabled in mode 0
 */
uint16_t spi_python480_read(uint16_t reg_addr)
{
    uint16_t slave_data;
    spi_start_transaction();
    _delay_us(SPI_CYCLE_PERIOD_US);
    spi_python480_write_register_addr(reg_addr, false);
    _delay_us(SPI_STATE_PERIOD_US);
    slave_data = spi_read_word();
    _delay_us(SPI_CYCLE_PERIOD_US);
    spi_stop_transaction();
    _delay_us(2 * SPI_CYCLE_PERIOD_US);
    return slave_data;
}

/* Descending into the madness of the Python 480 SPI protocol
 *
 * The Python 480 uses nine bit register addresses, transmitted most significant
 * bit first, with one bit of read/write direction, high for a write. The Python
 * 480 requires the clock to be low when idle. The clock should not toggle for
 * one clock period after the SS line is pulled low, and one clock cycle before
 * the SS line is deasserted. The polarity of the latching depends on whether
 * data is being read into or out of the sensor. When writing data to the sensor
 * the sensor latches data on the rising edge of the clock; when reading data
 * from the sensor the ATtiny should latch data on the falling edge of the
 * clock.
 *
 * We are using the Python 480 with the CMOS interface, which means `ratspi` <= 6.
 * The sensor oscillator is a 66.66 MHz, so the maximum SPI frequency is 11.11 MHz, which
 * is faster than the core frequency of the microcontroller. Thus, the maximum SPI
 * frequency that the ATtiny 816 is capable of, 2.5 MHz, is alright. The one cycle
 * minimum between SS and SCK should be satisfied by the delay between instructions
 * being executed by the ATtiny 816.
 *
 * The ATtiny should be in SPI mode 0 during write, and SPI mode 1 during read.
 *
 * Real SCK  is incorrectly wired as MISO (PC1)
 * Real MISO is incorrectly wired as MOSI (PC2)
 * Real MOSI is incorrectly wired as SCK  (PC0)
 * Real SSN  is correctly   wired as SSN  (PC3)
 */
void spi_init(void)
{
  PORTMUX.CTRLB |= PORTMUX_SPI0_bm;

  // Disable input buffering for SCK, MOSI, SS
  SPI_PORT.MOSICTRL = SPI_PORT.SCKCTRL = SPI_PORT.SSNCTRL = PORT_ISC_INPUT_DISABLE_gc;
  SPI_PORT.OUT = SCK_bm; // Set SSN high
  SPI_PORT.DIR = MOSI_bm | SSN_bm | SCK_bm; // SCK, MOSI, SS set to output
}

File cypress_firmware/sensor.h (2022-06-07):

/*
 ## Cypress FX3 Camera Kit header file (sensor.h)
 ## ===========================
 ##
 ##  Copyright Cypress Semiconductor Corporation, 2010-2012,
 ##  All Rights Reserved
 ##  UNPUBLISHED, LICENSED SOFTWARE.
 ##
 ##  CONFIDENTIAL AND PROPRIETARY INFORMATION
 ##  WHICH IS THE PROPERTY OF CYPRESS.
 ##
 ##  Use of this file is governed
 ##  by the license agreement included in the file
 ##
 ##     <install>/license/license.txt
 ##
 ##  where <install> is the Cypress software
 ##  installation root directory path.
 ##
 ## ===========================
*/

/* This file defines the parameters and the interface for the EV76C541 image
   sensor driver.
 */

#ifndef _INCLUDED_SENSOR_H_
#define _INCLUDED_SENSOR_H_

#include <cyu3types.h>

/* The SADDR line allows EV76C541 image sensor to select between two different I2C slave address.
   If the SADDR line is high, enable this #define to allow access to the correct I2C address for the sensor.
 */

/* I2C Slave address for the image sensor. */
#define SENSOR_ADDR_WR 0xB8             /* Slave address used to write sensor registers. */
#define SENSOR_ADDR_RD 0xB9             /* Slave address used to read from sensor registers. */

/* GPIO 20 on FX3 is used as SYNC output -- high during FV */
#define SENSOR_SYNC_GPIO 20

#define SENSOR_REG_CHIP_ID             0
#define SENSOR_REG_SOFT_RESET_ANALOG  10
#define SENSOR_REG_SEQ_GEN_CONFIG    192
#define SENSOR_REG_MULT_TIMER0       199
#define SENSOR_REG_FR_LENGTH0        200
#define SENSOR_REG_EXPOSURE0         201
#define SENSOR_REG_ANALOG_GAIN       204
#define SENSOR_REG_SYNC_CONFIG       206
#define SENSOR_REG_ROI0_X_CONFIG     256
#define SENSOR_REG_ROI0_Y_CONFIG     257
#define SENSOR_REG_ROI_CONFIG_LSB0   264
#define SENSOR_REG_ROI_CONFIG_LSB1   265

#define SENSOR_A_GAIN_TRANSL_1X   1
#define SENSOR_A_GAIN_TRANSL_2X   2
#define SENSOR_A_GAIN_TRANSL_3_5X 3

/* Communication over saturation channel */
#define SATURATION_RECORD_START 0x01
#define SATURATION_RECORD_END 0x02
#define SATURATION_INIT     0x03
#define SATURATION_FPS5     0x11
#define SATURATION_FPS10    0x12
#define SATURATION_FPS15    0x13
#define SATURATION_FPS20    0x14
#define SATURATION_FPS30    0x15
#define SATURATION_FPS60    0x16

extern CyU3PReturnStatus_t
SensorConfigureRoi1(
                      void);

extern CyU3PReturnStatus_t
SensorInit (
            void);

extern CyU3PReturnStatus_t
SensorStart (
    void);

extern CyU3PReturnStatus_t
SensorStop (
    void);

/* Function    : SensorIsOn
   Description : Check to see if the sensor is on
   Parameters  : None
*/
extern CyU3PReturnStatus_t
SensorIsOn (
            CyBool_t *isOn);

extern CyU3PReturnStatus_t
SensorDisable (
        void);

/* Function     : SensorScaling_HD720p_30fps
   Description  : Configure the EV76C541 sensor for 720p 30 fps video stream.
   Parameters   : None
 */
extern CyU3PReturnStatus_t
SensorScaling_808_608_30fps (
        void);

/* Function    : SensorI2CBusTest
   Description : Test whether the EV76C541 sensor is connected on the I2C bus.
   Parameters  : None
 */
extern CyU3PReturnStatus_t
SensorI2CBusTest (
        CyBool_t *connected);

/* Function    : SensorGetGain
   Description : Get the current gain setting from the EV76C541 sensor.
   Parameters  : None
 */
extern CyU3PReturnStatus_t
SensorGetGain (
               uint8_t *translated_gain);

/* Function    : SensorSetGain
   Description : Set the desired gain setting on the EV76C541 sensor.
   Parameters  :
                 gain - Desired gain level.
 */
extern CyU3PReturnStatus_t
SensorSetGain (
        uint8_t new_translated_gain);

#endif /* _INCLUDED_SENSOR_H_ */

/*[]*/

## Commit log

2021-09-08 added DAQ files
    [BOM.xlsx, Clocks.SchDoc, Connectors.SchDoc, Deserializer.SchDoc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]
2021-09-08 added commutator board
    [Commutator_Adaptor.brd, Commutator_Adaptor.sch]
2021-09-09 added body component files
    [baseplate.step, lower_subassembly.step, upper_subassembly.step]
2021-10-21 added pcb files
    [BOM.xlsx, I2C-to-SPI.SchDoc, Overall.SchDoc, PCB2.PcbDoc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]
2022-05-12 revised python pcb for speedy circuits, updated BOM
    [PCB2.PcbDoc]
2022-05-12 updated BOM, added gerbers for rev 1.1
    [BOM_substitutions_2022-05-11.xls, PCB2.GBL, PCB2.GBO, PCB2.GBP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]
2022-05-17 replaced opamp on PCB
    [BOM_substitutions_2022-05-11.xls, PCB2.GBL, PCB2.GBO, PCB2.GBP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]
2022-05-17 added new kiloscope baseplate design
    [baseplate.step]
2022-05-17 added main BOM
    [main_BOM.xlsx]
2022-05-17 updated main BOM
    [main_BOM.xlsx]
2022-05-17 added scope assembly instructions
2022-05-17 added commutator 3D model
    [commutator.step]
2022-05-25 updated commutator
    [BOM.xlsx, Commutator_Adaptor.brd, Commutator_Adaptor.sch]
2022-06-07 Add cypress firmware
    [frame_calculation.xlsx, osc_calculation.xlsx, period_calculation.xlsx, pll_calculation.xlsx]
2022-08-29 added attiny firmware
    [I2C-to-SPI.SchDoc, PCB2.PcbDoc, Python.SchDoc, Python_Auxiliary.SchDoc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]
2022-09-07 added pcb images
2022-09-08 split assembly instructions
2022-09-12 updated assembly instructions
2023-04-07 added images for assembly instructions
2024-09-11 exported assembly instructions as pdf
2025-01-30 updated kiloscope assembly instructions
